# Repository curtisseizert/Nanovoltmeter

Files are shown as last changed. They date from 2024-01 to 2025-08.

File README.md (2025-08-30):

# Nanovoltmeter
A low noise nanovoltmeter design files and code

The design includes five boards:
1. The nanovoltmeter main board
2. A SMPS daughter board to downconvert the battery voltage to the various power rails used in the design
3. A battery board with BMS for 4S 21700 cells
4. A rear panel board with battery charger
5. A front panel

This repository will also include the source code for the STM32U575 microcontroller that interfaces with the various peripherals.

ADR1399-boardfront
ADR1399-boardrear

Note: The current revision of the board does not work without modifications, but the schematic has been annotated to include these. This project should still be considered in a development state, but the entirety of the design is provided here for anyone seeking to draw upon this work in low-noise, high-resolution voltage sensing projects.

Curent Status
-------------
A revision C to the board is in a stage of occasional development as I finish another project. The new revision will seek to improve the robustness of the design, addressing issues such as the apparent sensitivity to common-mode noise, inadequate power protection leading to cascade failures with certain faults, and minor drift related to battery discharge. I am looking into an improved method of retrieving SPI data from ADC conversions that should allow operation at the maximum sample rate of the AD4030-24 (2 MSPS), to reduce noise and reduce the possibility of aliasing. The revision also includes a minor redesign of the key frontend amplifier to improve gain and stability. The ADR1399 reference option will be removed from this revision.

Version 2.0 of the FW improves handling of results and user inputs, as well as reduces the load on the CPU by making better use of DMA. Unit testing is ongoing and some features are not yet implemented, but they will be coming soon. The command structure uses a SCPI-like syntax but is not fully SCPI-compliant. The improved FW should facilitate more performance testing.

I have built two of these boards, one with an LTC6655 reference, the other with an ADR1399. I have tested the noise and offset performance of the latter both with internal shorts and an external 1 mV reference. Getting both boards to work has required some changes, and I have made the appropriate edits to a revision C schematic though I have not laid this out. The noise and temperature sensitivity of the LTC6655 board is superior for internal shorts. 

Design Background
-----------------

A proof of concept model of the input stage was previously prepared, which showed a flat NSD of approximately 1.2 nV/sqrt(Hz). At 1 sample per second, the peak to peak noise was about 15 nV. The temperature coefficient of the meter was approximately 1 nV/K, but sensitivity to temperature fluctuations was evident and the change in power dissipation as the battery discharged led to a drift of ca. 1 nV/h. This prototype also had a bias current of ~3 nA due to charge injection from the input modulator switch. This revision seeks to change those issues as follows:

1. The main power rails of the board are generated using low noise buck converters (LT8608S) and a Cuk converter on a shielded daughterboard so that the dropout of the on-board LDOs remains consistent through battery discharge
2. Improved layout reduced sensitivity to temperature changes. The input stage is contained in a shielding enclosure and is surrounded by isolation slots. Additionally, the largest power dissipators have been placed outside this shield on opposite sides.
3. The input switching is now handled by a low-capacitance quad MOSFET array (PE4140) using gate drive voltages independently generated with a quad DAC. In a model experiment, it has proven feasible to adjust the DAC switching levels and deadtimes to reduce bias current to <5 pA, though I need to do more work to optimize this aspect.
4. A fast, precision ADC (AD4030-24) now measures the offset error between switching cycles so a 16-bit DAC can control the offset voltage of the input differential amplifier by modulating the channel currents of the input JFETs. In the schematic, the trim range of the DAC is approximately +/-625uV (LSB = 20nV). The low gain of the trimming differential amplifier means the transconductance drops by <1% at the input extremes. This should allow measurement of the trim gain during instrument warmup for single-cycle settling of the control loop.
5. Digital implementation of the control loop also allows one to turn off autozeroing or run the input switching at very low frequencies to minimize charge injection.

Some additional features are:
1. Footprints for two types of voltage references: an ADR1399 for lowest noise/highest stability and an LTC6655 for lower power consumption
2. An optically isolated external trigger input for e.g., synchronizing clocking to powerline cycles.
3. Input protection that engages current limiting to 10 mA (typical, max: 15 mA) at a differential voltage of 2 V for protection against accidentally connecting up to 100V across the terminals. A GDT is included to provide transient protection against higher voltages.
4. Two input ranges: +/-2 mV and +/-20 mV.
5. Reduced power consumption (with LTC6655)

Principle of Operation
----------------------

SimplifiedSchematic

An input modulator (SW1) switch connects input and feedback signals alternately to the terminals of a high-gain, low-noise discrete JFET differential amplifier. The outputs of the differential amplifier are connected to the terminals of an operational amplifier (U10) via a synchronous demodulator (SW2). The output of the frontend is taken from this op amp. The ADC reads the output voltage from each phase of the modulator. If the difference between the two readings is larger than a deadband value, the controller increments or decrements the Vos DAC (U44) as needed to adjust the channel currents in the input differential amplifier to null the offset of the differential amplifier. The channel currents are controlled by a low-gain transconductance stage formed from U20. To null the offset and 1/f noise of the ADC and associated signal conditioning circuitry, a switch at the inputs to the ADC driver reverses the inputs to this block such that the modulator/demodulator operates at an integer multiple of the input switches for the ADC.

This topology has the effect of modulating the offset voltage (and 1/f noise) of the input stage up to the switching frequency but not modulating the input signal itself. This modulated error signal is minimized by the offset-nulling feedback loop, which dramatically reduces the power at the chopping frequency, and filtered using a cascaded integrator-comb (sinc) filter of user-selectable order (from 1 to 3). Because the input capacitance of the input stage JFETs is fairly large (ca. 75pF), nulling the offset of the differential amplifier also reduces current pulsation at the chopping frequency.

As such, the only theoretical source of offset, drift, or 1/f noise is the op amp connected to the demodulated differential amp outputs, and all these error sources are attentuated by the gain of the differential amplifier, which is about 3500. The input JFETs are paired with PNP BJTs Q16 and Q21 in a Szlikai-like topology to increase the transconductance of the input amplifier to enable it to operate at high gain. The value of drain resistors R91 and R100 is a compromise between noise, gain, and stability; at 133R, each of the eight JFETs operates with a drain current of ca. 1 mA, and the BJTs operate with a collector current of about 1 mA each. Larger resistor values slightly increase moise, increase gain, and decrease phase margin of the overall composite amplifier due to the increase in loop gain.  The op amp used in the design (an ADA4625-1) is a precision, low noise part with low offset and drift, and these error sources are negligible when attenuated by a factor of 3500. With typical spec sheet values, this op amp should contribute about 4 nV offset, 0.06 nV/K temperature coefficient, and give a 1/f noise corner of ca. 0.1 mHz. In practice, the effect of parasitics, especially thermal EMF proves to be a much larger error source, with an uncorrected offset voltage at the front panel of about 250 nV and a 1/f corner of slightly less than 1 mHz (depending on the stability of the ambient temperature). The NSD when measuring the (internally) shorted inputs is <1.2 nV/rt Hz, and with 10s sample periods I have observed p-p noise of just 1.36 nV over 10000 seconds.

ShortNoise_LTC6655_sinc2

Observations
------------

Modulator frequencies in the 600 - 2000 Hz seem to be ideal, and 1800 Hz is set as the default. The inclusion of the deadband in the offset correction loop is necessary to prevent artifacts that appear in the spectrum of the analog output. The key issue seems to be sensitivity to some noise source at low frequency (probably the SMPS, perhaps also 60 Hz pickup). Modulator frequencies up to 14.4 kHz are possible, but these lead to increases in noise as the settling time of the frontend and ADC signal conditioning circuits takes up an increasing percentage of the potential conversion time.

NVM B no deadband, 1 LSB inc, offsets
NSD without deadband, showing aliasing of V_os correction loop

The biggest limitation in the utility of the instrument is the considerable increase in noise and change in offset that occurs when something is connected to the front panel. This effect occurs regardless of whether the input relay is measuring an internal short. It seems most likely that the case, which is tied to protective earth via the USB cable shield is shifting in potential relative to circuit ground, and this is capacitively coupling to something sensitive. However, connecting the USB cable through an isolator, which disconnects the shield from PE, actually makes the noise situation worse rather than better. 

Implementation of a Sinc2 filter improved some apparent aliasing artifacts that were present in the spectrum at very low (<10 mHz) frequencies. Use of a Sinc3 filter did not lead to any noticeable improvents. The flatness of the noise spectrum (with an internal short) to below 1 mHz was very repeatable provided that environmental conditions were suitably stable.

ShortNoise_LTC6655_sinc1
ShortNoise_LTC6655_sinc2

While the nanovoltmenter has an offset temperature coefficient of <1 nV/K, it does show some sensitivity to changes in the rate of temperature change (i.e., the offset voltage correlates to the second derivative of temperature with respect to time). This makes sense because those changes lead to changes in temperature gradients across the board, which influences parasitic thermocouple behavior at the input. The power supply is also somewhat more efficient at lower input voltages, which leads to reduced heat dissipation as the batteries discharge, influencing the offset. In very long captures, such as the LTC6655 reference example shown below, this leads to a drift of <0.1 nV/h. It is notable that the overall drift in this 100h capture was only about 8 nV despite about 2.5 K fluctuation in input temperature over that time.

LongCapture_LTC6655_0p01SPS_sinc2
LongCapture_ADR1399_0p01SPS

The linearity of the amplifier is expected to be quite good as the offset correction loop keeps the input terminals of the frontend amplifier at the same voltage regardless of input. The main source of nonlinearity should be the gain setting resistors, as temperature changes due to increased power dissipation may lead to changes the resistor ratio and the gain of the frontend. To test the linearity of the amplifier, I used a highly accurate source based on an LTZ1000A and DAC11001B with a tested linearity error of <2 ppm and a 200K/20R divider to reduce the output voltage range to 0 to 1 mV. I averaged several 11 point sweeps over this range to obtain a maximum linearity error of 1.5 ppm. The averaging was necessary due the increased noise seen with something plugged in to the front panel. The increased sensitivity of the lower gain +/-20 mV range to external noise sources (probably due to reduced stability of the amplifier at lower gain) meant that determining linearity error for this range was not practical. In all measurements of external sources, I found it was optimal to wrap the test lead around a nanocrystalline toroid, which did reduce noise considerably.

LinearitySweep

Performance Reductions with External Measurements
-------------------------------------------------

Taken together, my observations about the difficulty of performing measurements with external sources are difficult to untangle and may point to multiple simultaneous issues. I have collected them here to try to provide some insight into this behavior and possible solutions:
1. The 40 dB gain range is more sensitive than the 60 dB gain range. The lower gain range has lower phase margin and still takes 60 dB gain at higher frequencies, as this was necessary to ensure stability of the amplifier at lower gain. This points to stability related problems, such as degradation of phase margin (leading to ringing, etc. after switching events) when the amplifier sees an inductive source impedance. Inductive sources present a considerable challenge with such amplifiers because of the large gate-source capacitance of the paralleled JFETs. This can give resonant gain with inductive inputs.
2. The improvement in performance when using a common mode choke on the input suggests an effect from frequencies well above the amplifier's passband. The inductance of the common mode choke was likely aorund 800 uH, which would present negligible impedance at 60 Hz.
3. I recorded spectra from the analog outputs with the instrument powered by a bench power supply to remove SMPS signals. With 60 dB gain on the frontend and the 10 nF input capacitor switched off, the peaks at harmonics of the chopping frequency were about 20 dB higher with an external short than with an internal short. This is presumably an effect of inductance at the input as there are ferrite beads in the input protection circuitry between the internal and external shorts. Some of these artifacts may lead to aliasing.
Internal Short Analog Output, Gain = 1000
NVM B Internal short Gain1000 Linear supply CapOff
External Short Analog Output, Gain = 1000NVM B External short Gain1000 Linear supply CapOff
4. Plugging a source into the input leads to a shift in offset with an internal short (ca. 200 nV). The source of this effect is not clear. The source mentioned in the linearity test section actually has an internal 100:1 attenuator for low voltages, but directly plugging the source into the NVM gave such large increases in noise that it would not be practical to measure ppm level offsets. The input connector is a LEMO-0S-304 type with the shell of the connector electically connected to the instrument chassis, which is itself connected to protective earth via the USB cable. In general, cables with the shield connected at both ends gave significantly poorer performance than those with the shield left unconnected at one end, suggesting that connection of the two chassis grounds was problematic despite their isolation from circuit ground. The use of nylon screws to connect the USB connector to the rear panel of the source (and hence remove the connection to protective earth) was necessary for reliable results in that case. Most of the sensitive circuitry of the input is very well shielded against electrostatic pickup by the use of board-level RF shields, but the input protection circuitry and switching relays, as well as the chopper demodulator and op amp, are outside of these shields. A ground loop is not necesasary to cause this effect, as it is observed even when an unconnected cable is plugged into the front panel. Some additional tests are necessary to determine the minimum configuration needed to cause this shift (e.g., does the behavior occur with just connection of the shell, or do the actual input leads (which provide a connection to the board) need to be connected as well? If it seems that additional shielding is needed to reduce this effect, it may be difficult to maintain the same form factor.

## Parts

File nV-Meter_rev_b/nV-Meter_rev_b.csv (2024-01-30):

Source: | C:\Users\Curtis\Documents\KiCAD\1fNoiseAmp\1fNoiseAmpRev12\1fNoiseAmpRev12.kicad_sch
Date: | 7/12/2023 12:35:11 AM
Tool: | Eeschema (6.0.11)
Generator: | C:\Program Files\KiCad\6.0\bin\scripting\plugins/bom_csv_grouped_by_value_with_fp.py
Component Count: | 376
Ref | Qnty | Value | Cmp name | Footprint | Description | Vendor
C1, C2, C3, C4, C5, C6, C7, C8, C11, C12, C13, C14, C16, C17, C18, C19, C20, C21, C66, C67, C84, | 21 | 100nF | C_Small | Capacitor_SMD:C_1206_3216Metric_Red | Unpolarized capacitor, small symbol
C9, C10, C15, C91, C92, | 5 | 47uF/16V | CP1_Small | Capacitor_Tantalum_SMD:CP_EIA-3528-12_Kemet-T | Polarized capacitor, small US symbol
C22, C23, C25, C26, C94, | 5 | 100nF X7R | C_Small | Capacitor_SMD:C_0603_1608Metric_red_outline | Unpolarized capacitor, small symbol
C24, C27, C28, C29, C30, C31, C32, C33, C34, C35, C36, C37, C38, C39, C40, C41, C42, C43, C44, C45, C46, C48, C49, C51, C52, C57, C64, C85, | 28 | 10nF | C_Small | Capacitor_SMD:C_0603_1608Metric_red_outline | Unpolarized capacitor, small symbol
C47, C63, | 2 | 10x470nF | C_Small | Capacitor_SMD:C_1206x10_3216Metric_Red | Unpolarized capacitor, small symbol
C50, | 1 | 33pF | C_Small | Capacitor_SMD:C_0603_1608Metric_red_outline | Unpolarized capacitor, small symbol | 81-GRM185C1H330GA01J
C53, C54, | 2 | 10pF C0G | C_Small | Capacitor_SMD:C_0603_1608Metric_red_outline | Unpolarized capacitor, small symbol
C55, C61, | 2 | 1nF | C_Small | Capacitor_SMD:C_0603_1608Metric_red_outline | Unpolarized capacitor, small symbol
C56, C62, | 2 | 47nF | C_Small | Capacitor_SMD:C_0805_2012Metric_Red_outline | Unpolarized capacitor, small symbol
C58, C65, | 2 | 470nF | C_Small | Capacitor_SMD:C_1206_3216Metric_Red | Unpolarized capacitor, small symbol
C59, C60, C78, | 3 | 10nF C0G | C_Small | Capacitor_SMD:C_0603_1608Metric_red_outline | Unpolarized capacitor, small symbol
C68, C69, | 2 | 10uF/25V | CP1_Small | Capacitor_Tantalum_SMD:CP_EIA-3528-12_Kemet-T | Polarized capacitor, small US symbol
C70, C71, | 2 | 33uF/25V | CP1_Small | Capacitor_Tantalum_SMD:CP_EIA-7343-31_Kemet-D | Polarized capacitor, small US symbol
C72, C73, | 2 | 10uF/35V | C_Small | Capacitor_SMD:C_1210_3225Metric | Unpolarized capacitor, small symbol
C74, C80, | 2 | 2.2uF X7R | C_Small | Capacitor_SMD:C_0805_2012Metric_Red_outline | Unpolarized capacitor, small symbol
C75, C76, | 2 | 22uF/50V | CP1_Small | Capacitor_Tantalum_SMD:CP_EIA-7343-31_Kemet-D | Polarized capacitor, small US symbol
C77, C79, | 2 | 10uF/25V | CP1_Small_Kelvin | Capacitor_Tantalum_SMD:CP_EIA-3528-12_Kemet-T_Kelvin | Polarized capacitor, small US symbol
C81, | 1 | 63x470nF/25V | C_Small | Capacitor_SMD:C_1206_Parallel | Unpolarized capacitor, small symbol
C82, | 1 | DNP | C_Small | Resistor_SMD:R_0603_1608Metric_red | Unpolarized capacitor, small symbol
C83, | 1 | 47nF/25V | C_Small | Capacitor_SMD:C_0805_2012Metric_Red_outline | Unpolarized capacitor, small symbol
C86, | 1 | 3.3pF C0G | C_Small | Capacitor_SMD:C_0603_1608Metric_red_outline | Unpolarized capacitor, small symbol | 81-GCM1885C2A3R3BA6D
C87, C88, C89, C90, | 4 | 100nF/50V | C_Small | Capacitor_SMD:C_1206_3216Metric_Red | Unpolarized capacitor, small symbol
C93, | 1 | 68pF C0G | C_Small | Capacitor_SMD:C_0603_1608Metric_red_outline | Unpolarized capacitor, small symbol | 81-GCM1885C2A680FA6D
D1, D2, D3, | 3 | ESDA6V1-5SC6 | ESDA6V1-5SC6 | Package_TO_SOT_SMD:SOT-23-6 | Quintuple bidirectional transil, Suppressor for ESD protection, 6V1 Breakdown, SOT-23-6
D4, D5, D6, D7, D8, D9, D10, D11, D19, D20, | 10 | DZ2S100X0L | DZ2S100X0L | Diode_SMD:D_SOD-523 | 150mW Silicon Planar Zener Diode, 10V, SOD-523 | 755-EDZVFHT2R10B
D12, D13, D14, D15, D17, D18, D22, D25, | 8 | BAV199 | BAV99 | Package_TO_SOT_SMD:SOT-23 | BAV99 High-speed switching diodes, SOT-23
D16, | 1 | LED | LED | LED_SMD:LED_Dialight_591 | Light emitting diode
D21, | 1 | BAV199DW | BAV199DW | Package_TO_SOT_SMD:SOT-363_SC-70-6 | Quad Surface Mount Low Leakage Diode, SOT-363
D23, D24, | 2 | MBR0540 | MBR0540 | Diode_SMD:D_SOD-123 | 40V 0.5A Schottky Power Rectifier Diode, SOD-123
H1, H2, H3, H4, | 4 | MountingHole_Pad | MountingHole_Pad | MountingHole:MountingHole_2.2mm_M2_Pad_Via | Mounting Hole with connection
J1, | 1 | Conn_Coaxial | Conn_Coaxial | Connector_Coaxial:SMA_Molex_73251-2120_EdgeMount_Horizontal | coaxial connector (BNC, SMA, SMB, SMC, Cinch/RCA, LEMO, ...)
J2, | 1 | Conn_01x02 | Conn_01x02 | Connector_PinHeader_2.54mm:PinHeader_1x02_P2.54mm_Vertical | Generic connector, single row, 01x02, script generated (kicad-library-utils/schlib/autogen/connector/)
J3, | 1 | IDC_HDR | Conn_02x10_Odd_Even | Connector_PinHeader_1.27mm:PinHeader_2x10_P1.27mm_Vertical | Generic connector, double row, 02x10, odd/even pin numbering scheme (row 1 odd numbers, row 2 even numbers), script generated (kicad-library-utils/schlib/autogen/connector/)
J4, | 1 | PIN_JMP | Conn_02x03_Odd_Even | Connector_PinHeader_2.54mm:PinHeader_2x03_P2.54mm_Vertical | Generic connector, double row, 02x03, odd/even pin numbering scheme (row 1 odd numbers, row 2 even numbers), script generated (kicad-library-utils/schlib/autogen/connector/)
J5, J23, | 2 | Conn_Coaxial | Conn_Coaxial | Connector_Coaxial:SMA_Molex_73251-135_SMT_Vertical | coaxial connector (BNC, SMA, SMB, SMC, Cinch/RCA, LEMO, ...)
J6, J7, J8, J9, J10, J11, J12, J13, J14, J15, J16, J17, | 12 | ShieldClip | Conn_01x01 | RF_Shielding:RF_Shield_Clip_Harwin_Mini | Generic connector, single row, 01x01, script generated (kicad-library-utils/schlib/autogen/connector/)
J18, J19, | 2 | RF_Shield_Two_Pieces | RF_Shield_Two_Pieces | RF_Shielding:Laird_Technologies_BMI-S-230-F_50.8x38.1mm | Two-piece EMI RF shielding cabinet | 739-BMI-S-230-F
J20, J21, | 2 | SMA_OUT | Conn_Coaxial | Connector_Coaxial:SMA_Molex_73251-2120_EdgeMount_Horizontal | coaxial connector (BNC, SMA, SMB, SMC, Cinch/RCA, LEMO, ...)
J22, | 1 | Micro-Fit 3.0 43650-0310 | Conn_01x03_MountingPin | Connector_Molex:Molex_Micro-Fit_3.0_43650-0310_1x03-1MP_P3.00mm_Horizontal_PnP | Generic connectable mounting pin connector, single row, 01x03, script generated (kicad-library-utils/schlib/autogen/connector/) | 538-43650-0310
K1, K2, K3, K4, | 4 | G6KU-2 | G6KU-2 | Relay_SMD:Relay_DPDT_Omron_G6K-2G-Y | Miniature 2-pole relay, Single-winding Latching | 653-G6KU-2G-Y-DC5
Q1, Q3, Q5, Q7, Q22, | 5 | BSS84 | BSS84 | Package_TO_SOT_SMD:SOT-23 | -0.13A Id, -50V Vds, P-Channel MOSFET, SOT-23
Q2, Q4, Q6, Q8, | 4 | BSS123 | BSS123 | Package_TO_SOT_SMD:SOT-23 | 0.17A Id, 100V Vds, N-Channel MOSFET, SOT-23
Q9, Q10, Q11, Q14, Q15, | 5 | MMBF4117 | MMBF4117 | Package_TO_SOT_SMD:SOT-23 | Low leakage N-Channel JFET, SOT-23
Q12, | 1 | SiS443DN | SiS443DN | Package_SO:Vishay_PowerPAK_1212-8_Single | -35A Id, -40V Vds, P-Channel MOSFET, PowerPAK 1212-8 Single
Q13, | 1 | SiS862ADN | SiS862ADN | Package_SO:Vishay_PowerPAK_1212-8_Single | 52A Id, 60V Vds, 7.2mOhm Rds(ON), N-Channel MOSFET, PowerPAK 1212-8 Single
Q16, Q17, Q20, Q24, Q27, Q29, Q31, Q33, Q35, Q37, Q39, Q41, Q43, Q45, Q47, Q49, Q51, Q53, | 18 | MMBT3904 | MMBT3904 | Package_TO_SOT_SMD:SOT-23 | 0.2A Ic, 40V Vce, Small Signal NPN Transistor, SOT-23
Q18, Q23, Q26, Q28, Q30, Q32, Q34, Q36, Q38, Q40, Q42, Q44, Q46, Q48, Q50, Q52, | 16 | JFE2140 | JFE2140 | Package_SO:SOIC-8_3.9x4.9mm_P1.27mm | Ultra-low Noise, Matched, Dual, Low-Gate Current, Discrete Audio N-Channel JFET
Q19, | 1 | HN4C51J | HN4C51J | Package_TO_SOT_SMD:SOT-23-5_red | 120V 100mA Common Base Audio Frequency GP NPN Pair
Q21, Q25, | 2 | HN4A51J | HN4A51J | Package_TO_SOT_SMD:SOT-23-5_red | 120V 100mA Common Base Audio Frequency GP PNP Pair
R1, | 1 | 6k02 0.1% | R_US | Resistor_SMD:R_1206_3216Metric_red | Resistor, US symbol | 667-ERA-8AEB6041V
R2, | 1 | 240R 0.1% | R_US | Resistor_SMD:R_1206_3216Metric_red | Resistor, US symbol | 667-ERA-8AEB241V
R3, R67, R68, | 3 | 0R5 | R_US | Resistor_SMD:R_1206_3216Metric_red | Resistor, US symbol
R4, R5, R6, R7, R8, R9, R12, R13, R14, R15, R58, | 11 | 10k | R_US | Resistor_SMD:R_0603_1608Metric_red | Resistor, US symbol
R10, R11, R16, R17, R18, R19, R20, R21, R22, R23, R63, R64, R90, R91, | 14 | 1M | R_US | Resistor_SMD:R_0603_1608Metric_red | Resistor, US symbol
R24, R25, R54, R55, R56, R59, R60, R100, R111, | 9 | 49R9 | R_US | Resistor_SMD:R_0603_1608Metric_red | Resistor, US symbol
R26, | 1 | 10M | R_US | Resistor_SMD:R_1206_3216Metric_red | Resistor, US symbol
R27, R28, R103, | 3 | 1k 0.1% | R_US | Resistor_SMD:R_0805_2012Metric_red | Resistor, US symbol
R29, | 1 | 49R9 0.1% | R_US | Resistor_SMD:R_0805_2012Metric_red | Resistor, US symbol
R30, R31, R49, R51, R86, | 5 | 1k | R_US | Resistor_SMD:R_0603_1608Metric_red | Resistor, US symbol
R32, | 1 | 47R5 | R_US | Resistor_SMD:R_0805_2012Metric_red | Resistor, US symbol | 667-ERA-6AEB47R5V
R33, | 1 | 1k24 0.1% | R_US | Resistor_SMD:R_0805_2012Metric_red | Resistor, US symbol | 71-TNPW08051K24BEEA
R34, | 1 | 240R 0.1% | R_US | Resistor_SMD:R_0805_2012Metric_red | Resistor, US symbol | 754-RG2012N-241-WT1
R35, | 1 | 220R | R_US | Resistor_SMD:R_0805_2012Metric_red | Resistor, US symbol | 667-ERA-6VEB2200V
R36, | 1 | 2k67 | R_US | Resistor_SMD:R_0603_1608Metric_red | Resistor, US symbol | 754-RR0816P-2671D42H
R37, | 1 | 56k2 | R_US | Resistor_SMD:R_0603_1608Metric_red | Resistor, US symbol | 754-RR0816P-5622D73C
R38, | 1 | 2k4 0.1% | R_US | Resistor_SMD:R_0805_2012Metric_red | Resistor, US symbol | 667-ERA-6ARW242V
R39, | 1 | 9k53 | R_US | Resistor_SMD:R_0603_1608Metric_red | Resistor, US symbol
R40, R84, | 2 | 200k | R_US | Resistor_SMD:R_0603_1608Metric_red | Resistor, US symbol | 754-RR0816P-204D
R41, | 1 | 2M87 | R_US | Resistor_SMD:R_0603_1608Metric_red | Resistor, US symbol
R42, R43, | 2 | 2M49 | R_US | Resistor_SMD:R_0603_1608Metric_red | Resistor, US symbol | 603-RC0603FR-072M49L
R44, | 1 | 1M8 | R_US | Resistor_SMD:R_0603_1608Metric_red | Resistor, US symbol | 603-AC0603FR-071M8L
R45, R97, | 2 | 887R | R_US | Resistor_SMD:R_0603_1608Metric_red | Resistor, US symbol | 754-RR0816P-8870D92A
R46, | 1 | 18k7 | R_US | Resistor_SMD:R_0603_1608Metric_red | Resistor, US symbol | 754-RR0816P-1872D27C
R47, R76, R77, R82, | 4 | 28k7 | R_US | Resistor_SMD:R_0603_1608Metric_red | Resistor, US symbol
R48, | 1 | 604k | R_US | Resistor_SMD:R_0603_1608Metric_red | Resistor, US symbol | 603-RT0603DRE07604KL
R50, R61, R62, | 3 | 100k | R_US | Resistor_SMD:R_0603_1608Metric_red | Resistor, US symbol
R52, | 1 | 499k | R_US | Resistor_SMD:R_1206_3216Metric_red | Resistor, US symbol | 667-ERA-8AEB4993V
R53, | 1 | 4M7 | R_US | Resistor_SMD:R_1206_3216Metric_red | Resistor, US symbol | 594-MCA1206MD4704BP1
R57, | 1 | 10M | R_US | Resistor_SMD:R_0603_1608Metric_red | Resistor, US symbol
R65, R66, | 2 | 2R | R_US | Resistor_SMD:R_0603_1608Metric_red | Resistor, US symbol
R69, | 1 | 43k 0.1% | R_US | Resistor_SMD:R_1206_3216Metric_red | Resistor, US symbol | 667-ERA-8AEB433V
R70, | 1 | 53k6 | R_US | Resistor_SMD:R_1206_3216Metric_red | Resistor, US symbol | 667-ERA-8AEB53R6V
R71, | 1 | 499k | R_US | Resistor_SMD:R_0603_1608Metric_red | Resistor, US symbol
R72, R74, | 2 | 30k1 | R_US | Resistor_SMD:R_0603_1608Metric_red | Resistor, US symbol
R73, | 1 | 360k | R_US | Resistor_SMD:R_0603_1608Metric_red | Resistor, US symbol | 754-RR0816P-364D
R75, | 1 | 100M | R_US | Resistor_SMD:R_1206_3216Metric_red | Resistor, US symbol | 708-HVCB1206FKC100M
R78, | 1 | 7k5 | R_US | Resistor_SMD:R_0603_1608Metric_red | Resistor, US symbol | 754-RR0816P-752D
R79, R81, R85, R89, R92, R94, R95, R96, R98, R99, R102, R105, R106, R107, R108, R109, R110, | 17 | 3k3 | R_US | Resistor_SMD:R_0603_1608Metric_red | Resistor, US symbol | 754-RR0816P-332D
R80, R83, | 2 | 330 0.1% | R_US | Resistor_SMD:R_0805_2012Metric_red | Resistor, US symbol
R87, R88, | 2 | 33k 0.1% | R_US | Resistor_SMD:R_0805_2012Metric_red | Resistor, US symbol
R93, | 1 | 100R | R_US | Resistor_SMD:R_0603_1608Metric_red | Resistor, US symbol
R101, | 1 | 4R7 | R_US | Resistor_SMD:R_0603_1608Metric_red | Resistor, US symbol | 603-RT0603FRE074R7L
R104, | 1 | 4R99 0.1% | R_US | Resistor_SMD:R_0805_2012Metric_red | Resistor, US symbol
RN1, RN2, RN3, | 3 | 33R | R_Pack04 | Resistor_SMD:R_Array_Convex_4x0402 | 4 resistor network, parallel topology
RN4, | 1 | 9k/1k | Voltage_Divider | Package_TO_SOT_SMD:SOT-23 | Voltage divider | 71-MPMT10019001AT1
RN5, RN6, | 2 | 10k/10k | Voltage_Divider | Package_TO_SOT_SMD:SOT-23 | Voltage divider
RN7, RN8, RN9, | 3 | 1M | R_Pack04 | Resistor_SMD:R_Array_Convex_4x0402 | 4 resistor network, parallel topology
TP1, TP2, TP3, TP4, TP5, TP6, TP7, TP8, TP9, TP10, TP11, TP12, TP13, TP14, TP15, TP16, TP17, TP18, TP19, TP20, TP21, TP22, TP23, TP24, TP25, TP26, TP27, TP28, TP29, TP30, TP31, | 31 | TestPoint | TestPoint | TestPoint:TestPoint_Pad_D1.0mm | test point
U1, U2, U4, | 3 | TLV1812D | TLV1812D | Package_SO:SOIC-8_3.9x4.9mm_P1.27mm | Dual Rail-to-Rail Input Comparators with Push-Pull Output, SOIC-8
U3, U7, U12, U15, U16, | 5 | DG636EEQ | DG636EEQ_4 | Package_SO:TSSOP-14_4.4x5mm_P0.65mm | 0.3 pC Charge Injection, 100 pA Leakage
U5, U21, | 2 | OPA140 | OPA140 | Package_SO:MSOP-8_3x3mm_P0.65mm | High-Precision, Low-Noise, RRO, 11 MHz JFET Op Amp
U6, U8, U10, U11, U20, | 5 | ADA4622-2 | OPA2145 | Package_SO:MSOP-8_3x3mm_P0.65mm | Dual Operational Amplifiers, DIP-8/SOIC-8/TSSOP-8/VSSOP-8
U9, U13, | 2 | ADA4807-1 | ADA4807-1 | Package_TO_SOT_SMD:SOT-23-6_red | Single Rail-to-Rail Input/Output Amplifiers, with disable, SC-70-6/SOT-23-6
U14, | 1 | TLC555xD | TLC555xD | Package_SO:SOIC-8_3.9x4.9mm_P1.27mm | Single LinCMOS Timer, 555 compatible, SOIC-8 | 700-ICM7555ISAT
U17, | 1 | LT3042xMSE | LT3042xMSE | Package_SO:MSOP-10EP-3x3_P0.5mm_EP_thermal_vias_opt | 200mA, Adjustable, Ultralow Noise, Ultrahigh PSRR RF Linear Regulator, MSOP-10
U18, | 1 | LP2985-3.3 | LP2985-3.3 | Package_TO_SOT_SMD:SOT-23-5 | 150mA 16V Low-noise Low-dropout Regulator With Shutdown, 3.3V output voltage, SOT-23-5
U19, | 1 | LT3093xMSE | LT3093xMSE | Package_SO:MSOP-12-1EP_3x4mm_P0.65mm_EP1.65x2.85mm_ThermalVias_opt | -200mA, Adjustable, Ultralow Noise, Ultrahigh PSRR RF Negative Linear Regulator, MSOP-12
U22, | 1 | 74AUP1G02 | 74AUP1G02 | Package_TO_SOT_SMD:SOT-353_SC-70-5 | Single NOR Gate, Low-Voltage CMOS | 595-SN74AUP1G02DCKT

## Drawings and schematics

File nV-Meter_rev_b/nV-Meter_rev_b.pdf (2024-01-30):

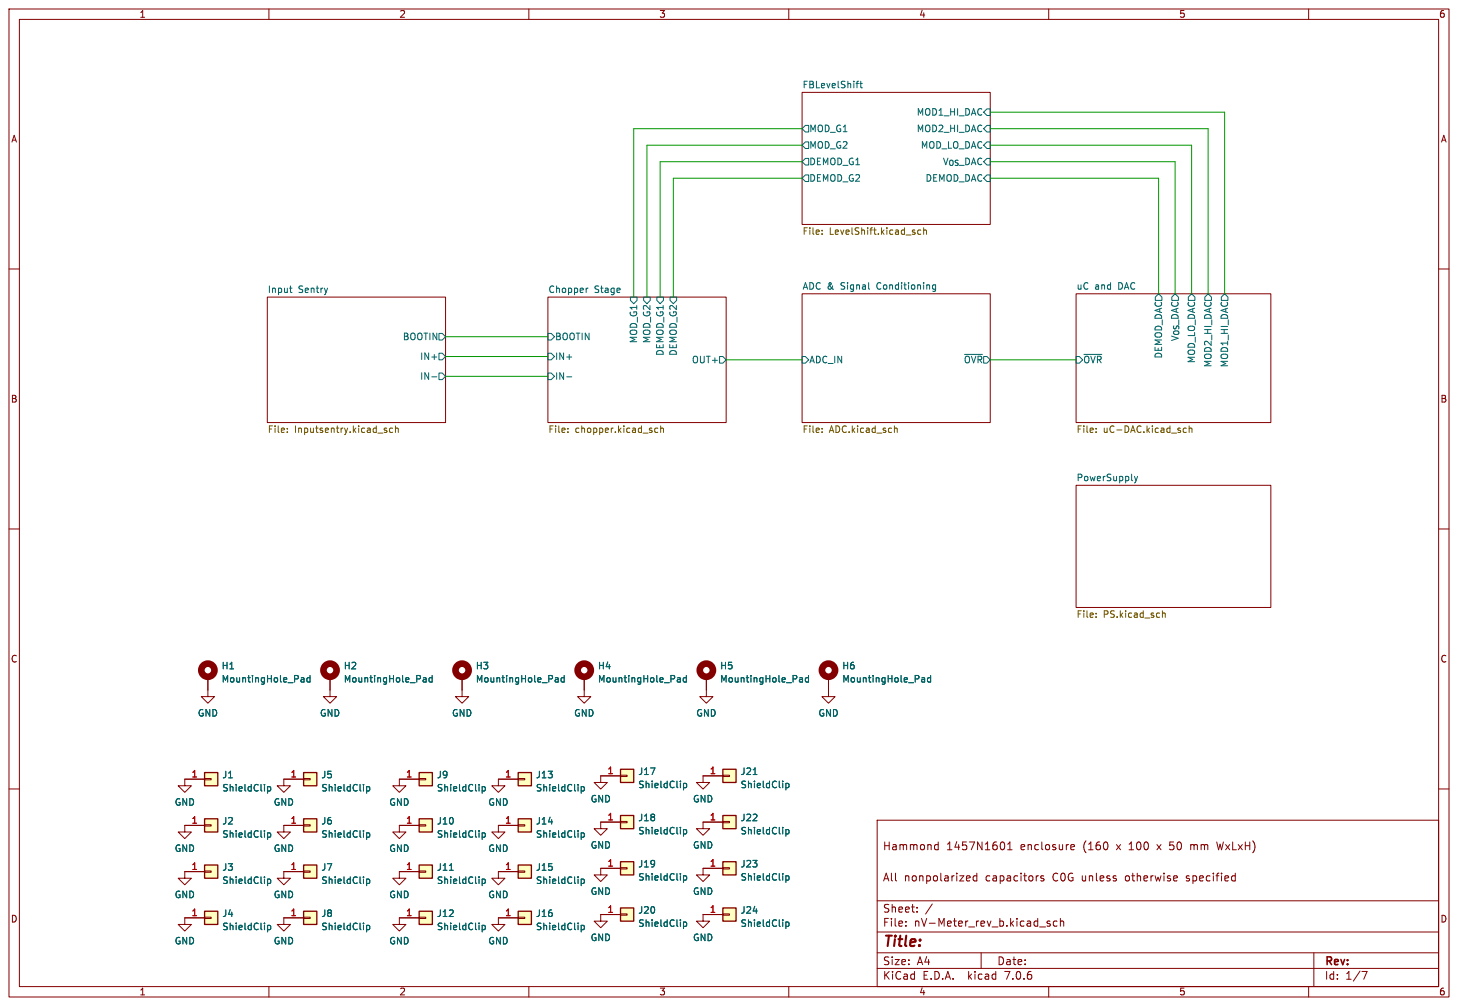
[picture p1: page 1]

Chopper Stage File: chopper.kicad_sch H4 MountingHole_Pad

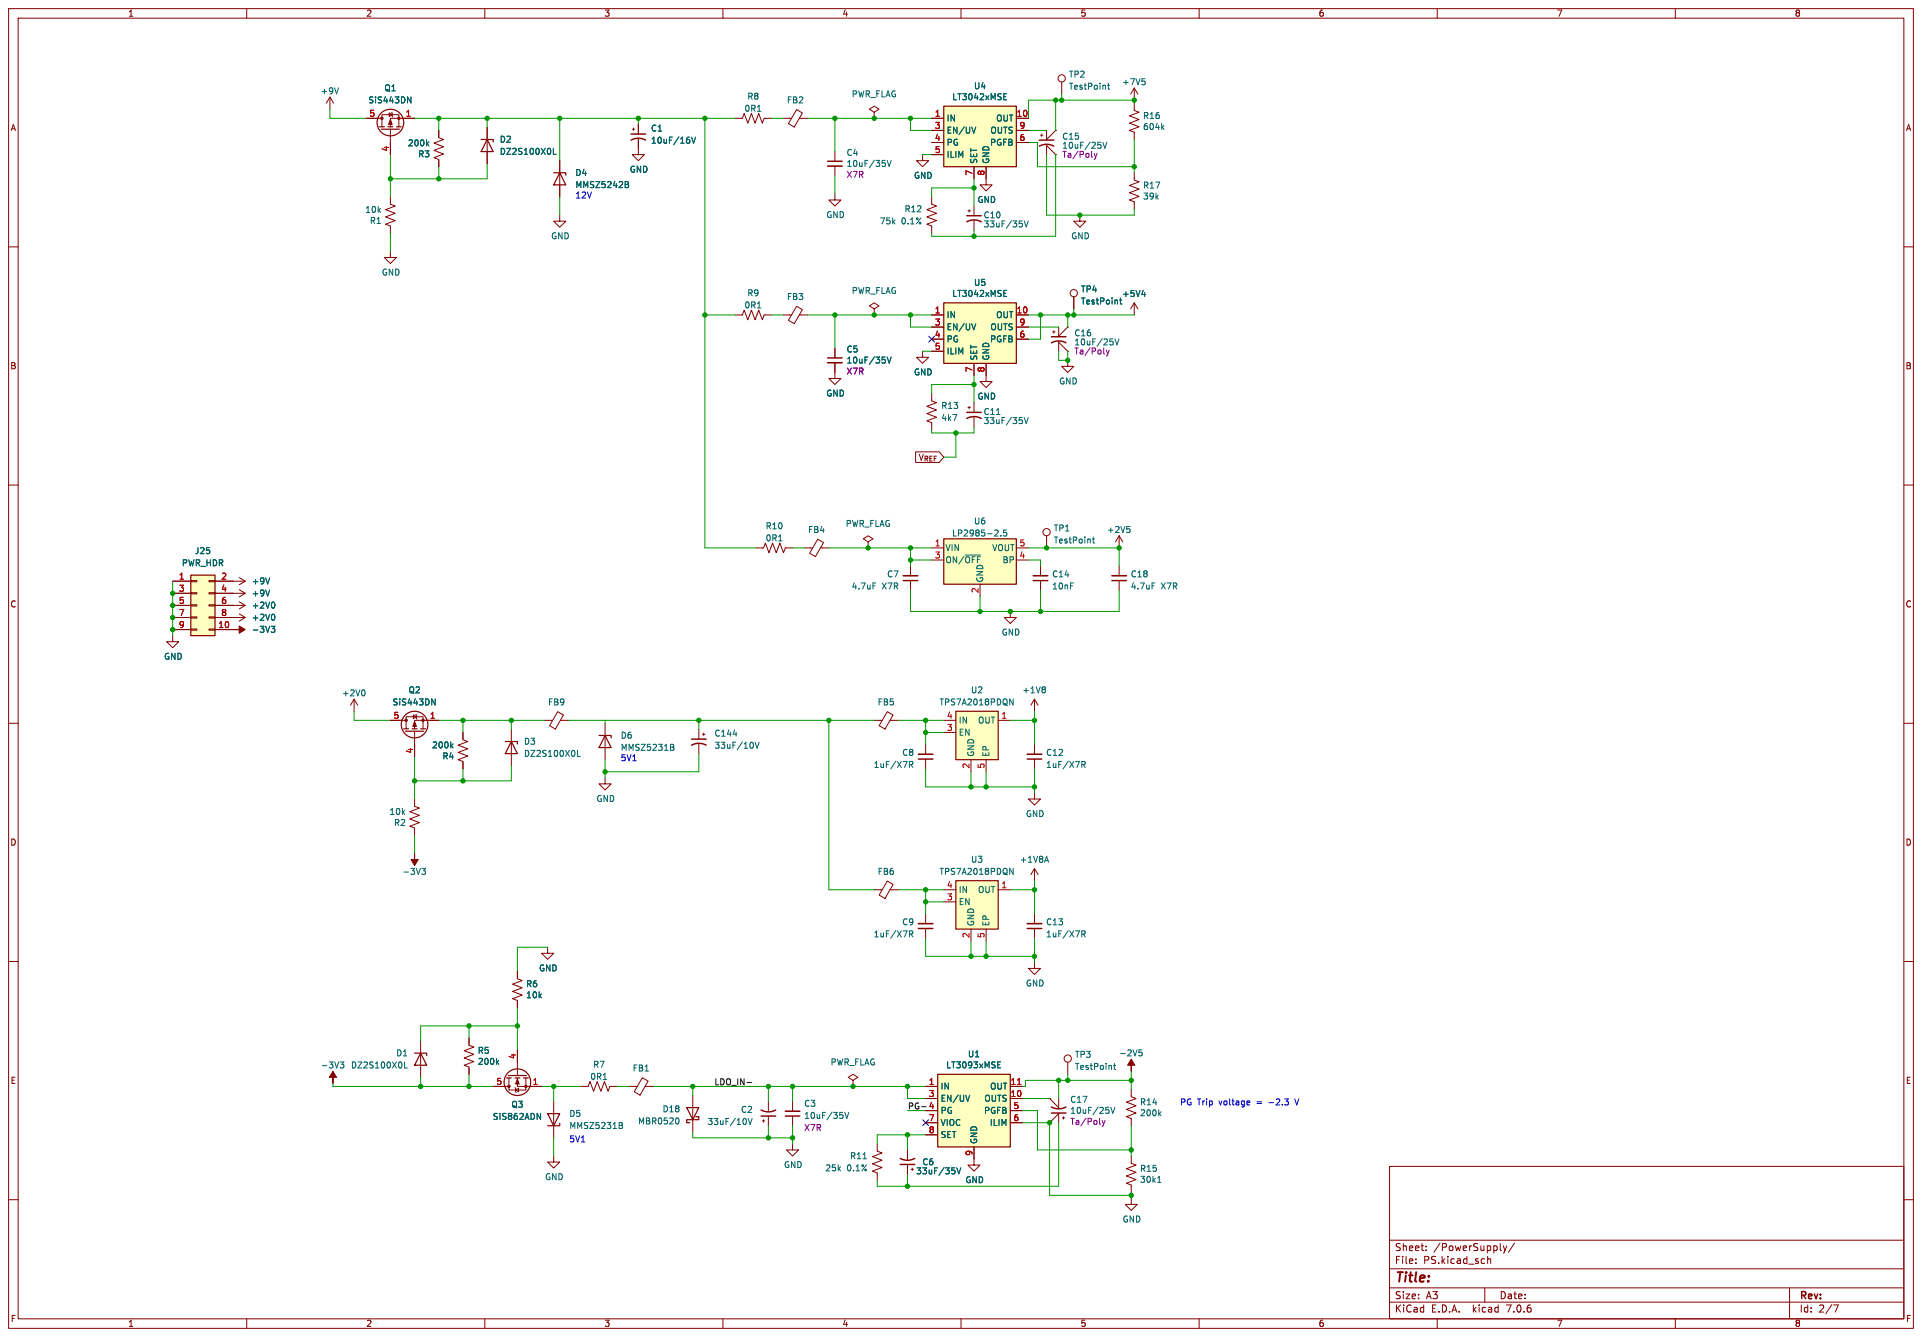
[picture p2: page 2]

2 ON/~{OFF} 3 BP 4 VOUT 5 U6

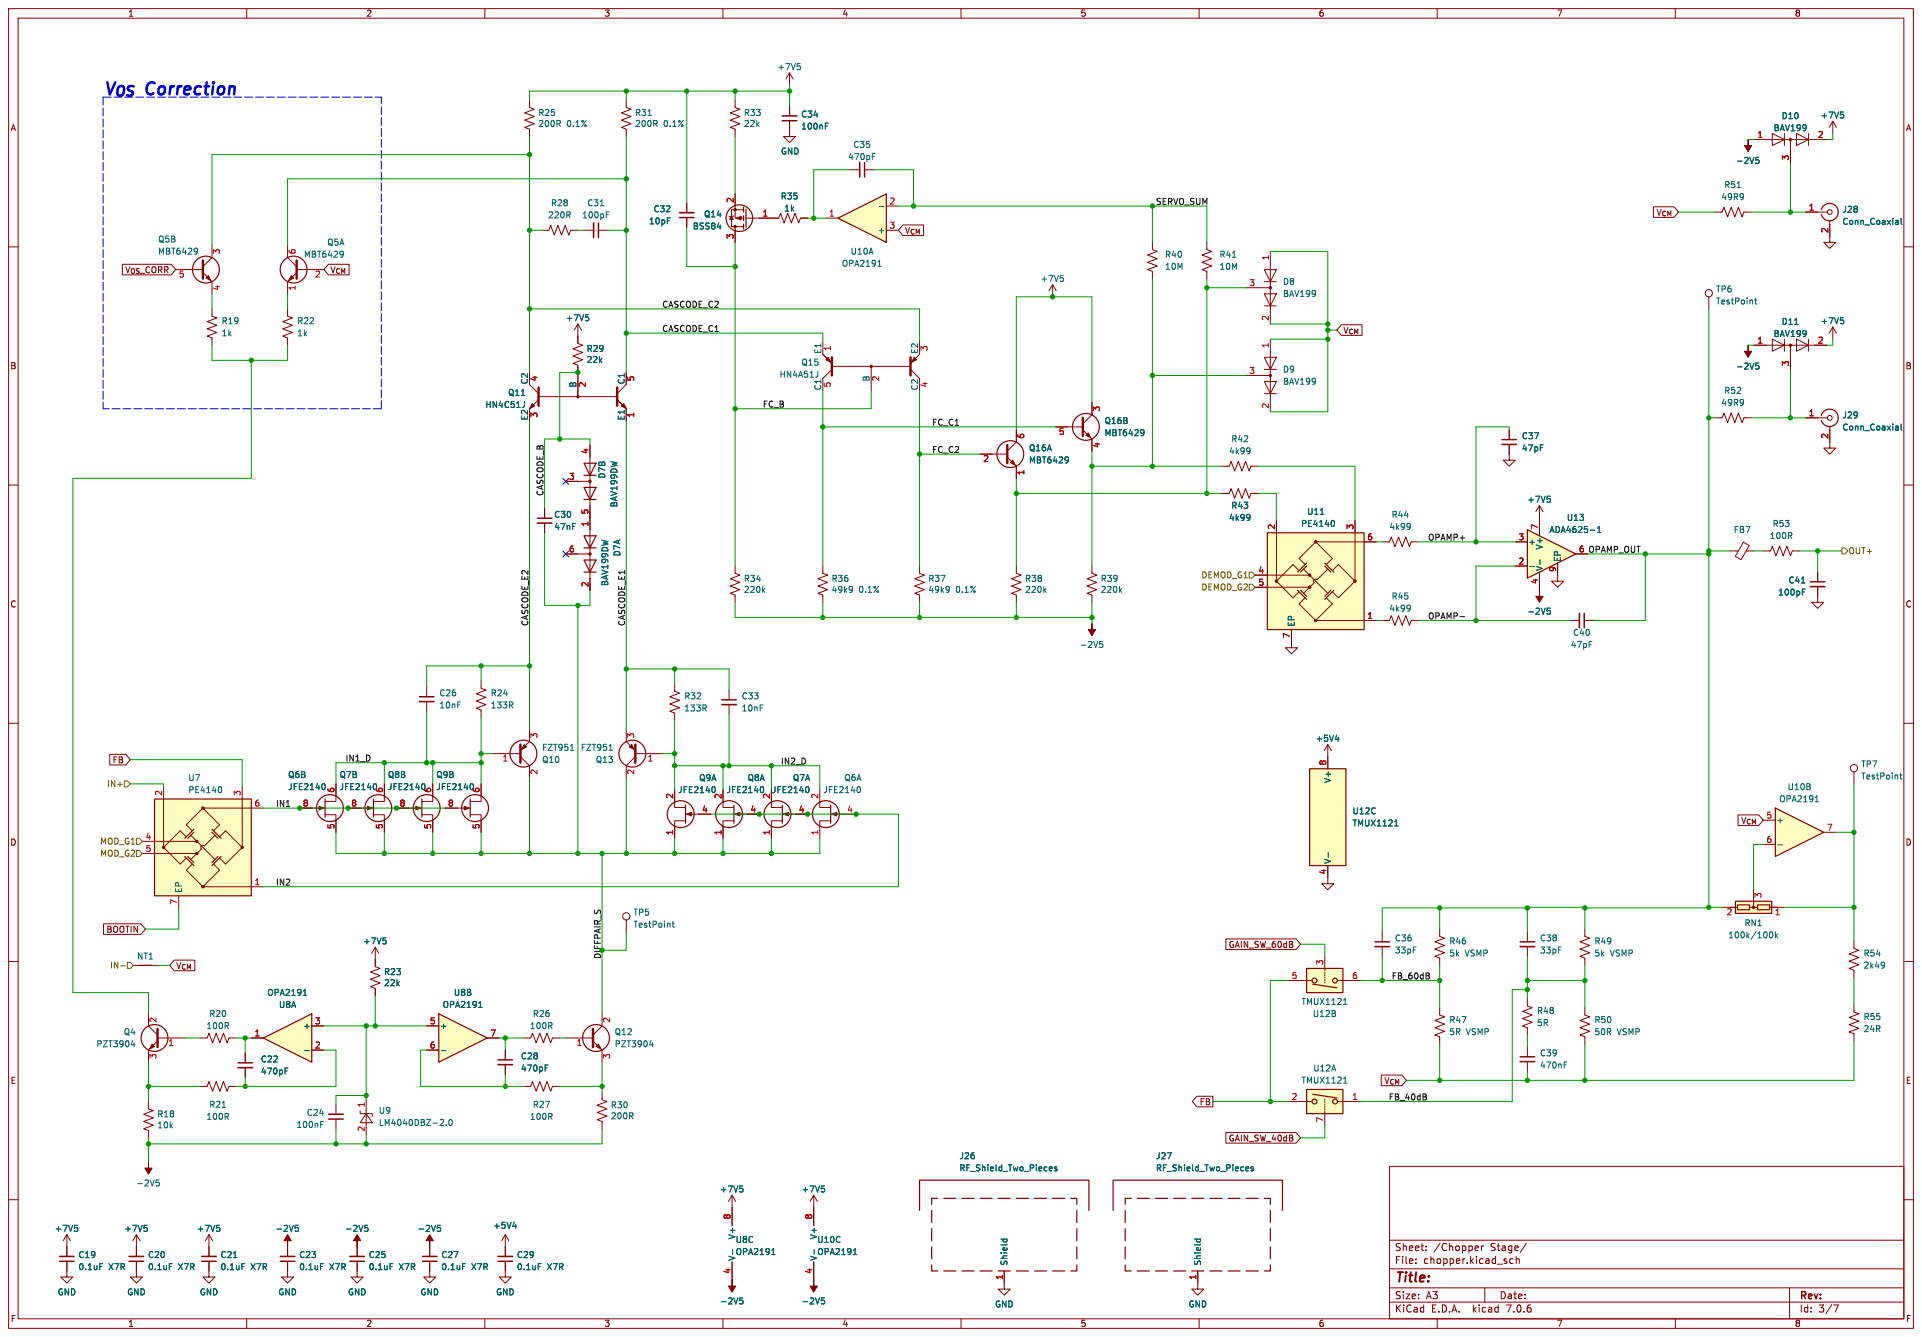
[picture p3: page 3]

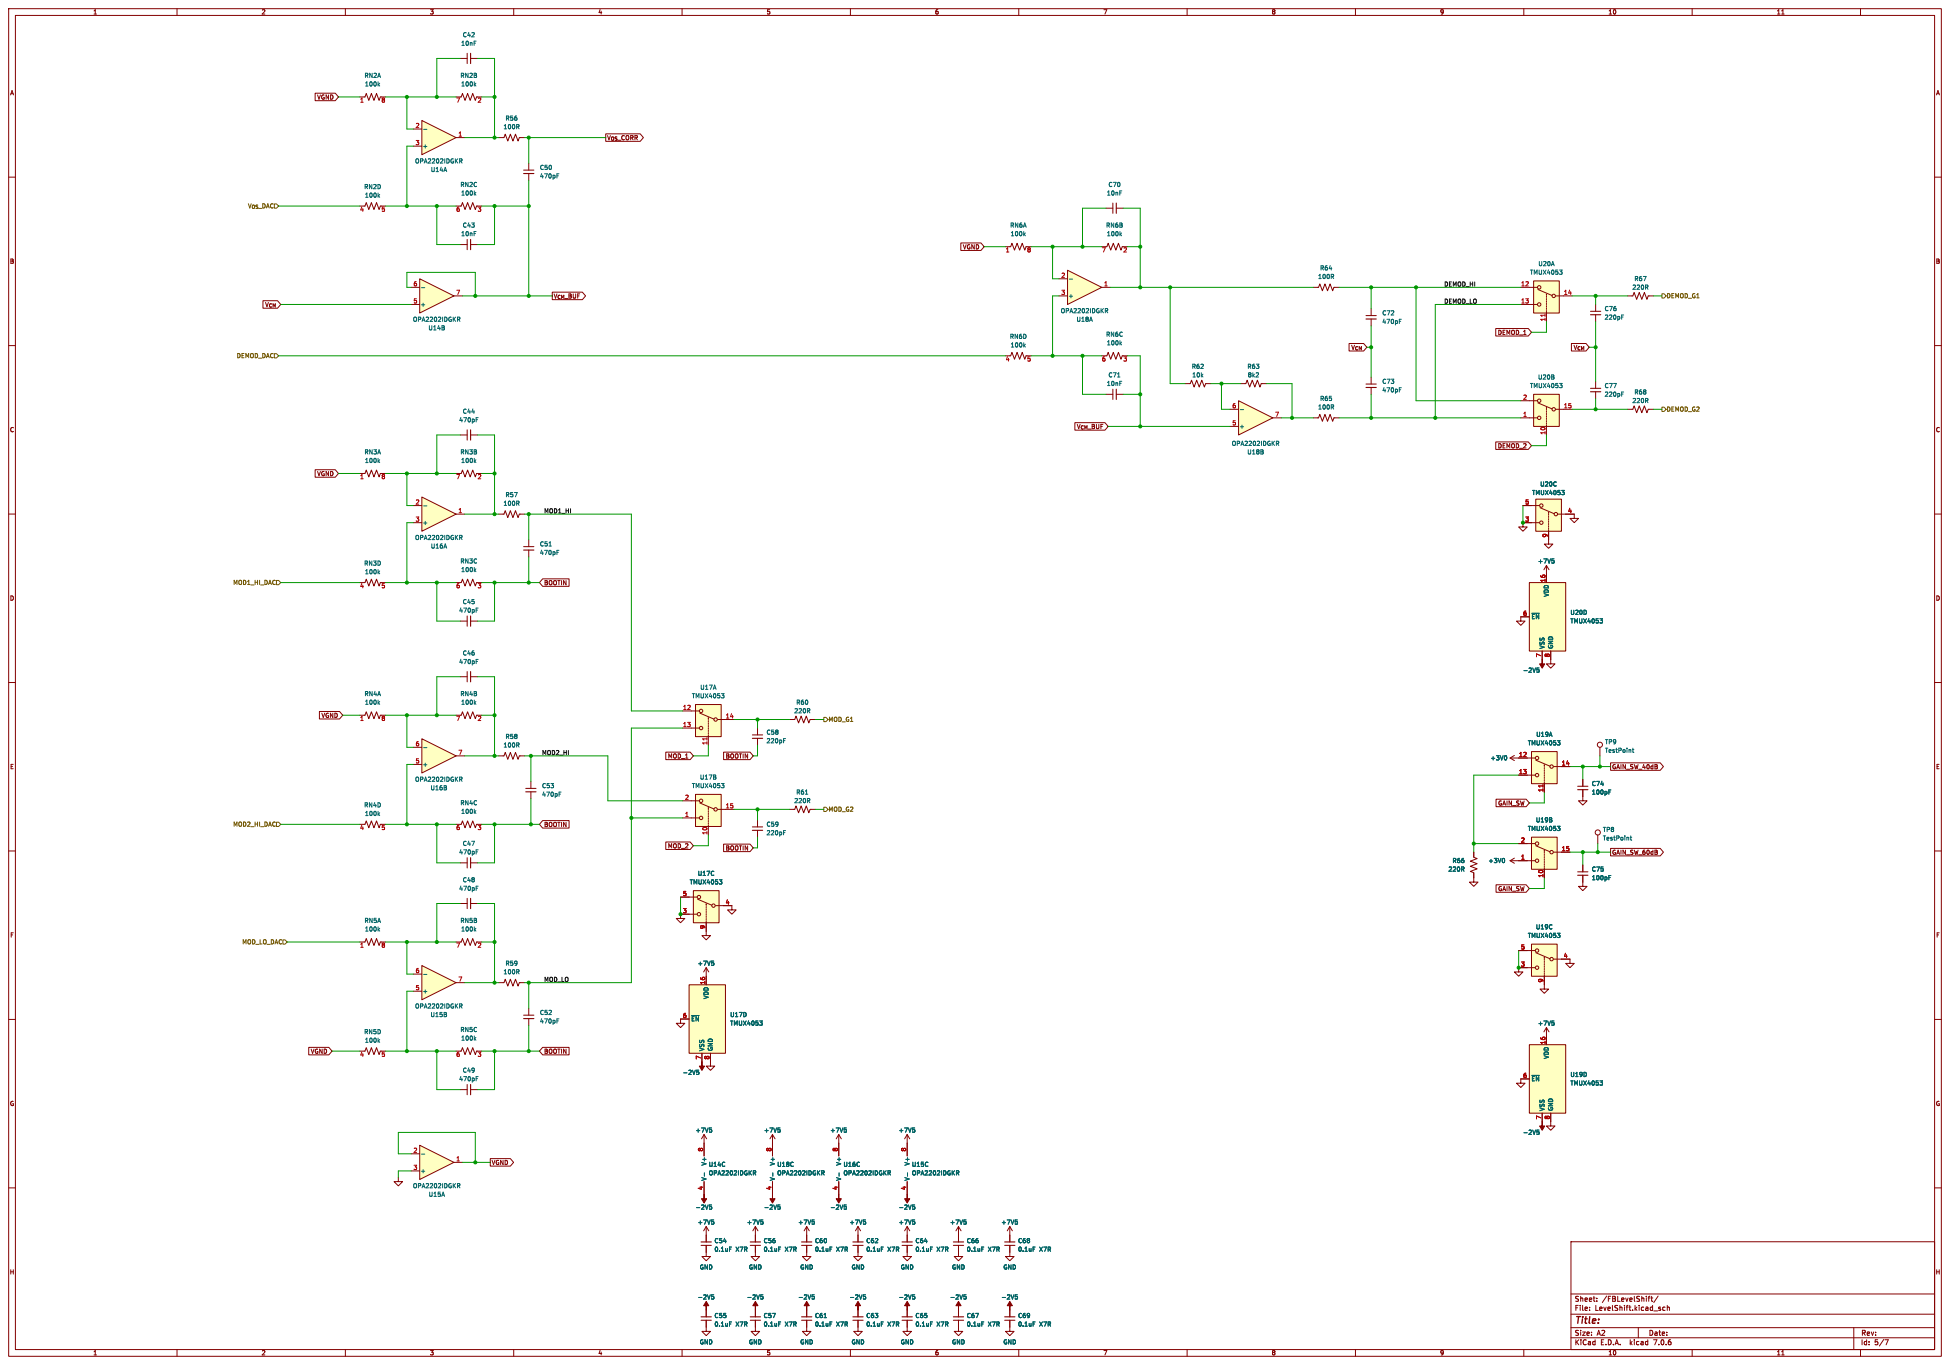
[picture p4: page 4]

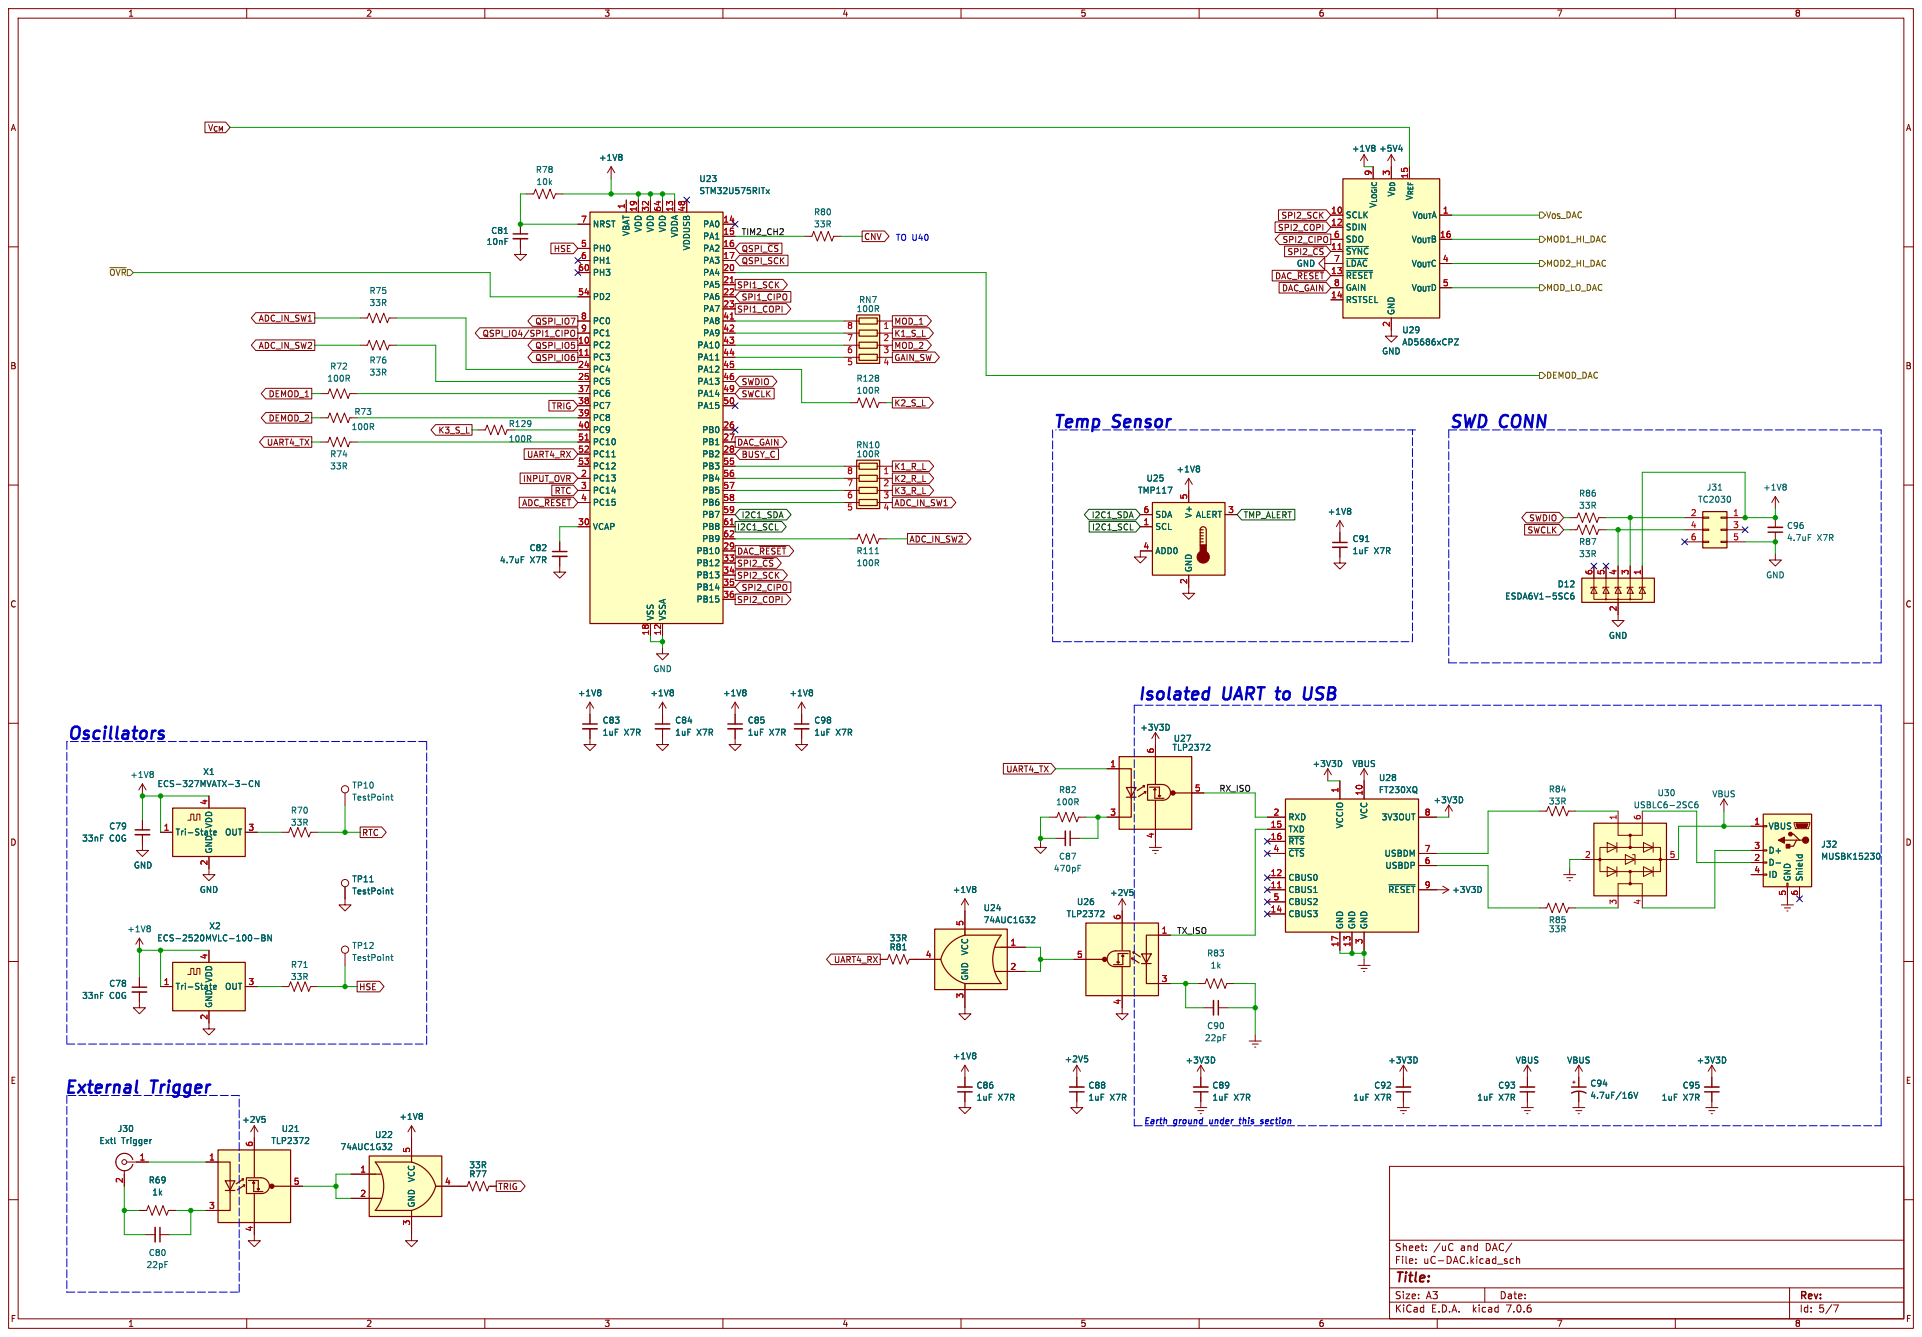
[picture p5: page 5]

2 V_{DD} 3 V_{OUT}C4 V_{OUT}D5 SDO 6 ~{LDAC} 7 GAIN 8 V_{LOGIC} 9 U27 TLP2372

2 V_{DD} 3 V_{OUT}C4 V_{OUT}D5 SDO 6 ~{LDAC} 7 GAIN 8 V_{LOGIC} 9 U29 AD5686xCPZ

1 PC2 10 PC3 11 VSSA 12 VDDA 13 PA0 14 PA1 15 PA2 16 PA3 17 VSS 18 VDD 19 PC13 2 PA4 20 PA5 21 PA6 22 PA7 23 PC4 24 PC5 25 PB0 26 PB1 27 PB2 28 PB10 29 PC14 3 VCAP 30 VDD 32 PB12 33 PB13 34 PB14 35 PB15 36 PC6 37 PC7 38 PC8 39 PC15 4 PC9 40 PA8 41 PA9 42 PA10 43 PA11 44 PA12 45 PA13 46 VDDUSB 48 PA14 49 PH0 5 PA15 50 PC10 51 PC11 52 PC12 53 PD2 54 PB3 55 PB4 56 PB5 57 PB6 58 PB7 59 PH1 6 PH3 60 PB8 61 PB9 62 VDD 64 NRST 7 PC0 8 PC1 9 U23 STM32U575RITx R80
33R GND

1 PC2 10 PC3 11 VSSA 12 VDDA 13 PA0 14 PA1 15 PA2 16 PA3 17 VSS 18 VDD 19 PC13 2 PA4 20 PA5 21 PA6 22 PA7 23 PC4 24 PC5 25 PB0 26 PB1 27 PB2 28 PB10 29 PC14 3 VCAP 30 VDD 32 PB12 33 PB13 34 PB14 35 PB15 36 PC6 37 PC7 38 PC8 39 PC15 4 PC9 40 PA8 41 PA9 42 PA10 43 PA11 44 PA12 45 PA13 46 VDDUSB 48 PA14 49 PH0 5 PA15 50 PC10 51 PC11 52 PC12 53 PD2 54 PB3 55 PB4 56 PB5 57 PB6 58 PB7 59 PH1 6 PH3 60 PB8 61 PB9 62 VDD 64 NRST 7 PC0 8 PC1 9 C82

Isolated UART to USB

1 VCC 10 CBUS1 11 CBUS0 12 GND 13 CBUS3 14 TXD 15 ~{RTS} 16 GND 17 RXD 2 GND

Earth ground under this section External Trigger

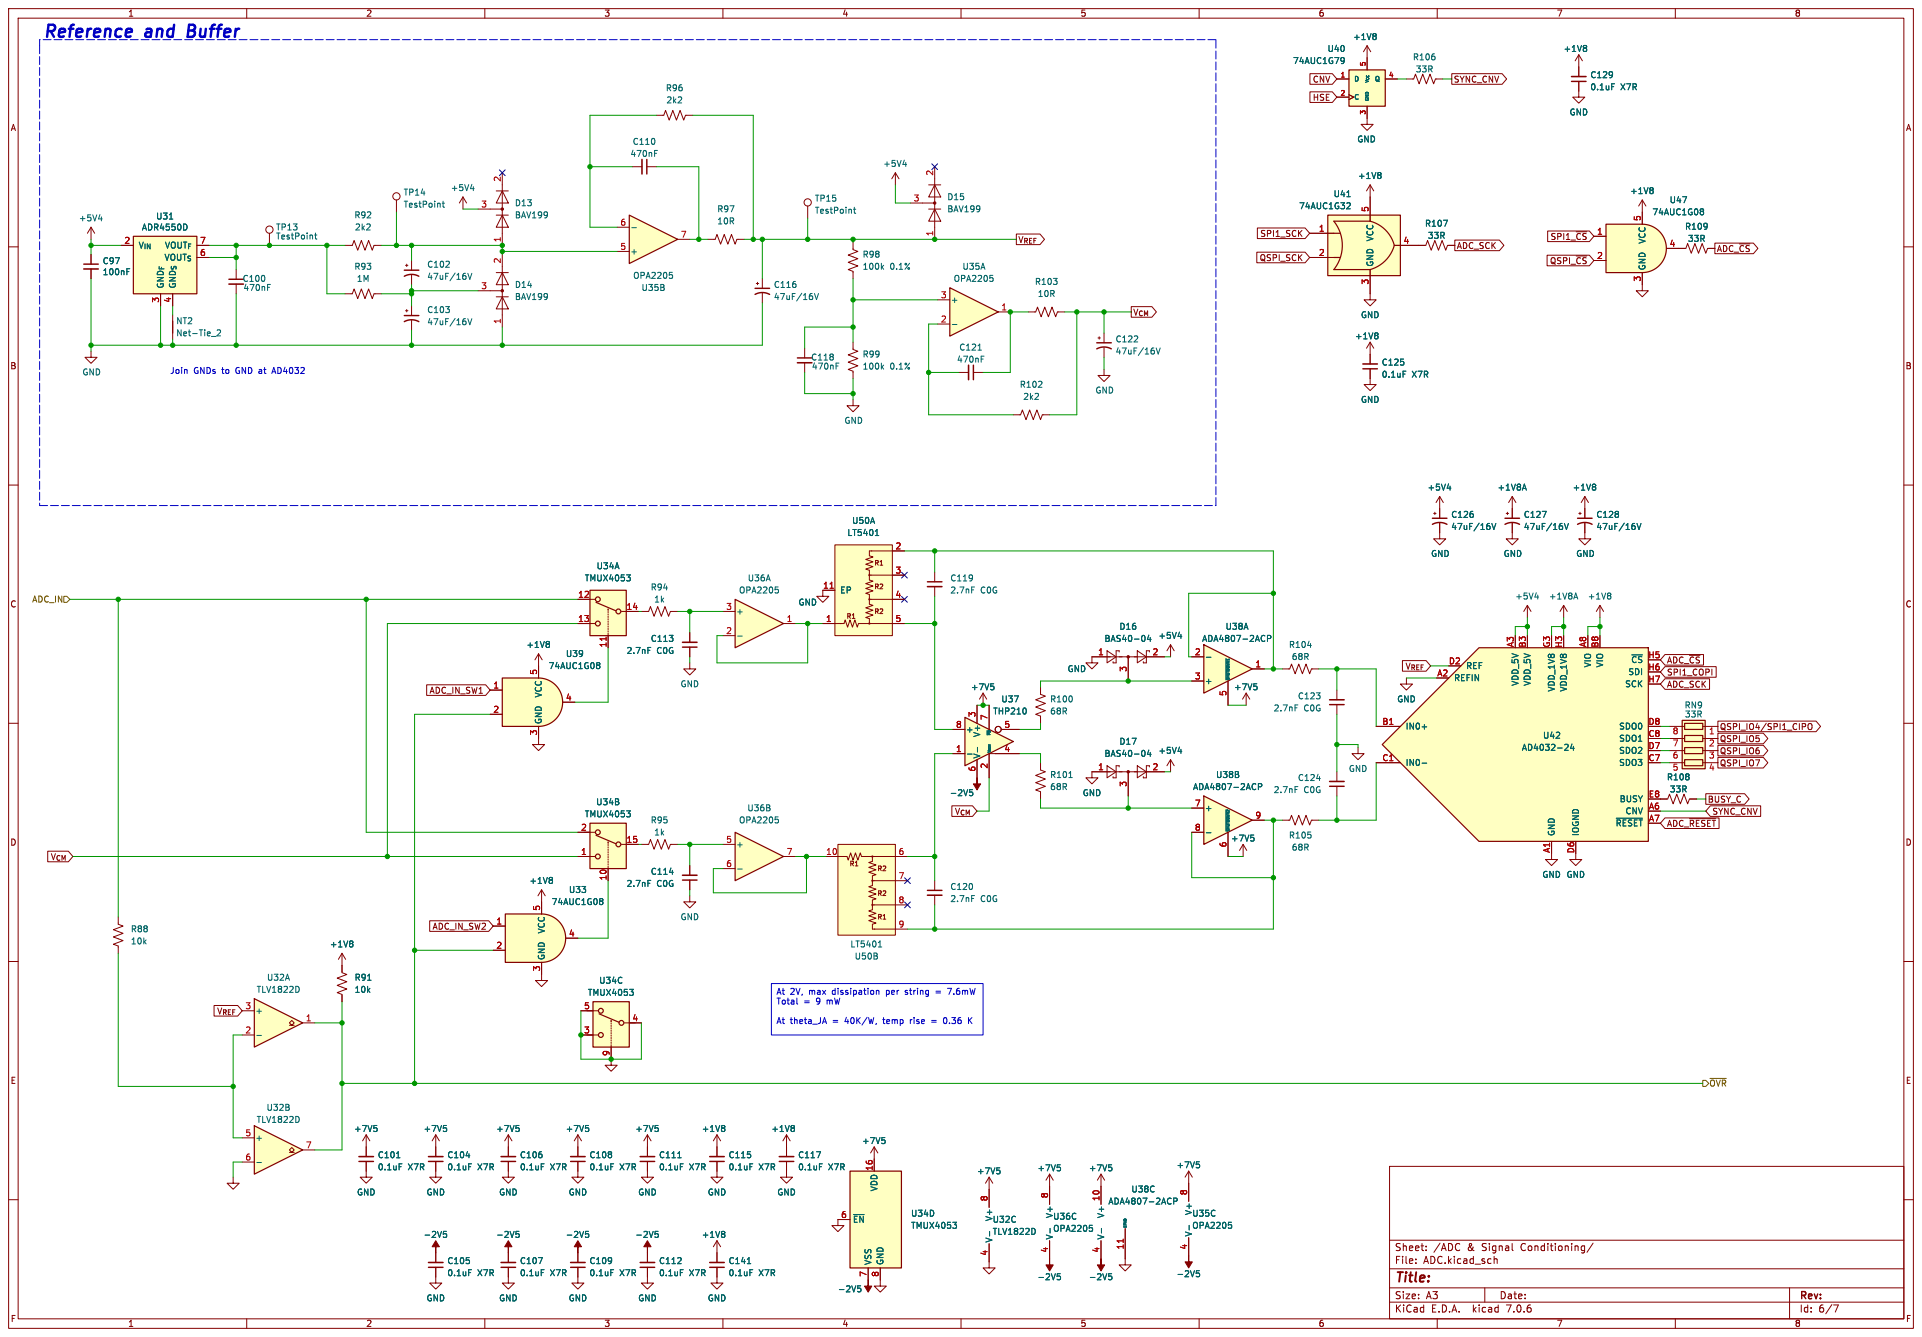
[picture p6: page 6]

Join GNDs to GND at AD4032

~{CS}H5 SDI H6 SCK H7 GND A1 REFIN A2

Id: 6/7 Title: File: ADC.kicad_sch Sheet: /ADC & Signal Conditioning/

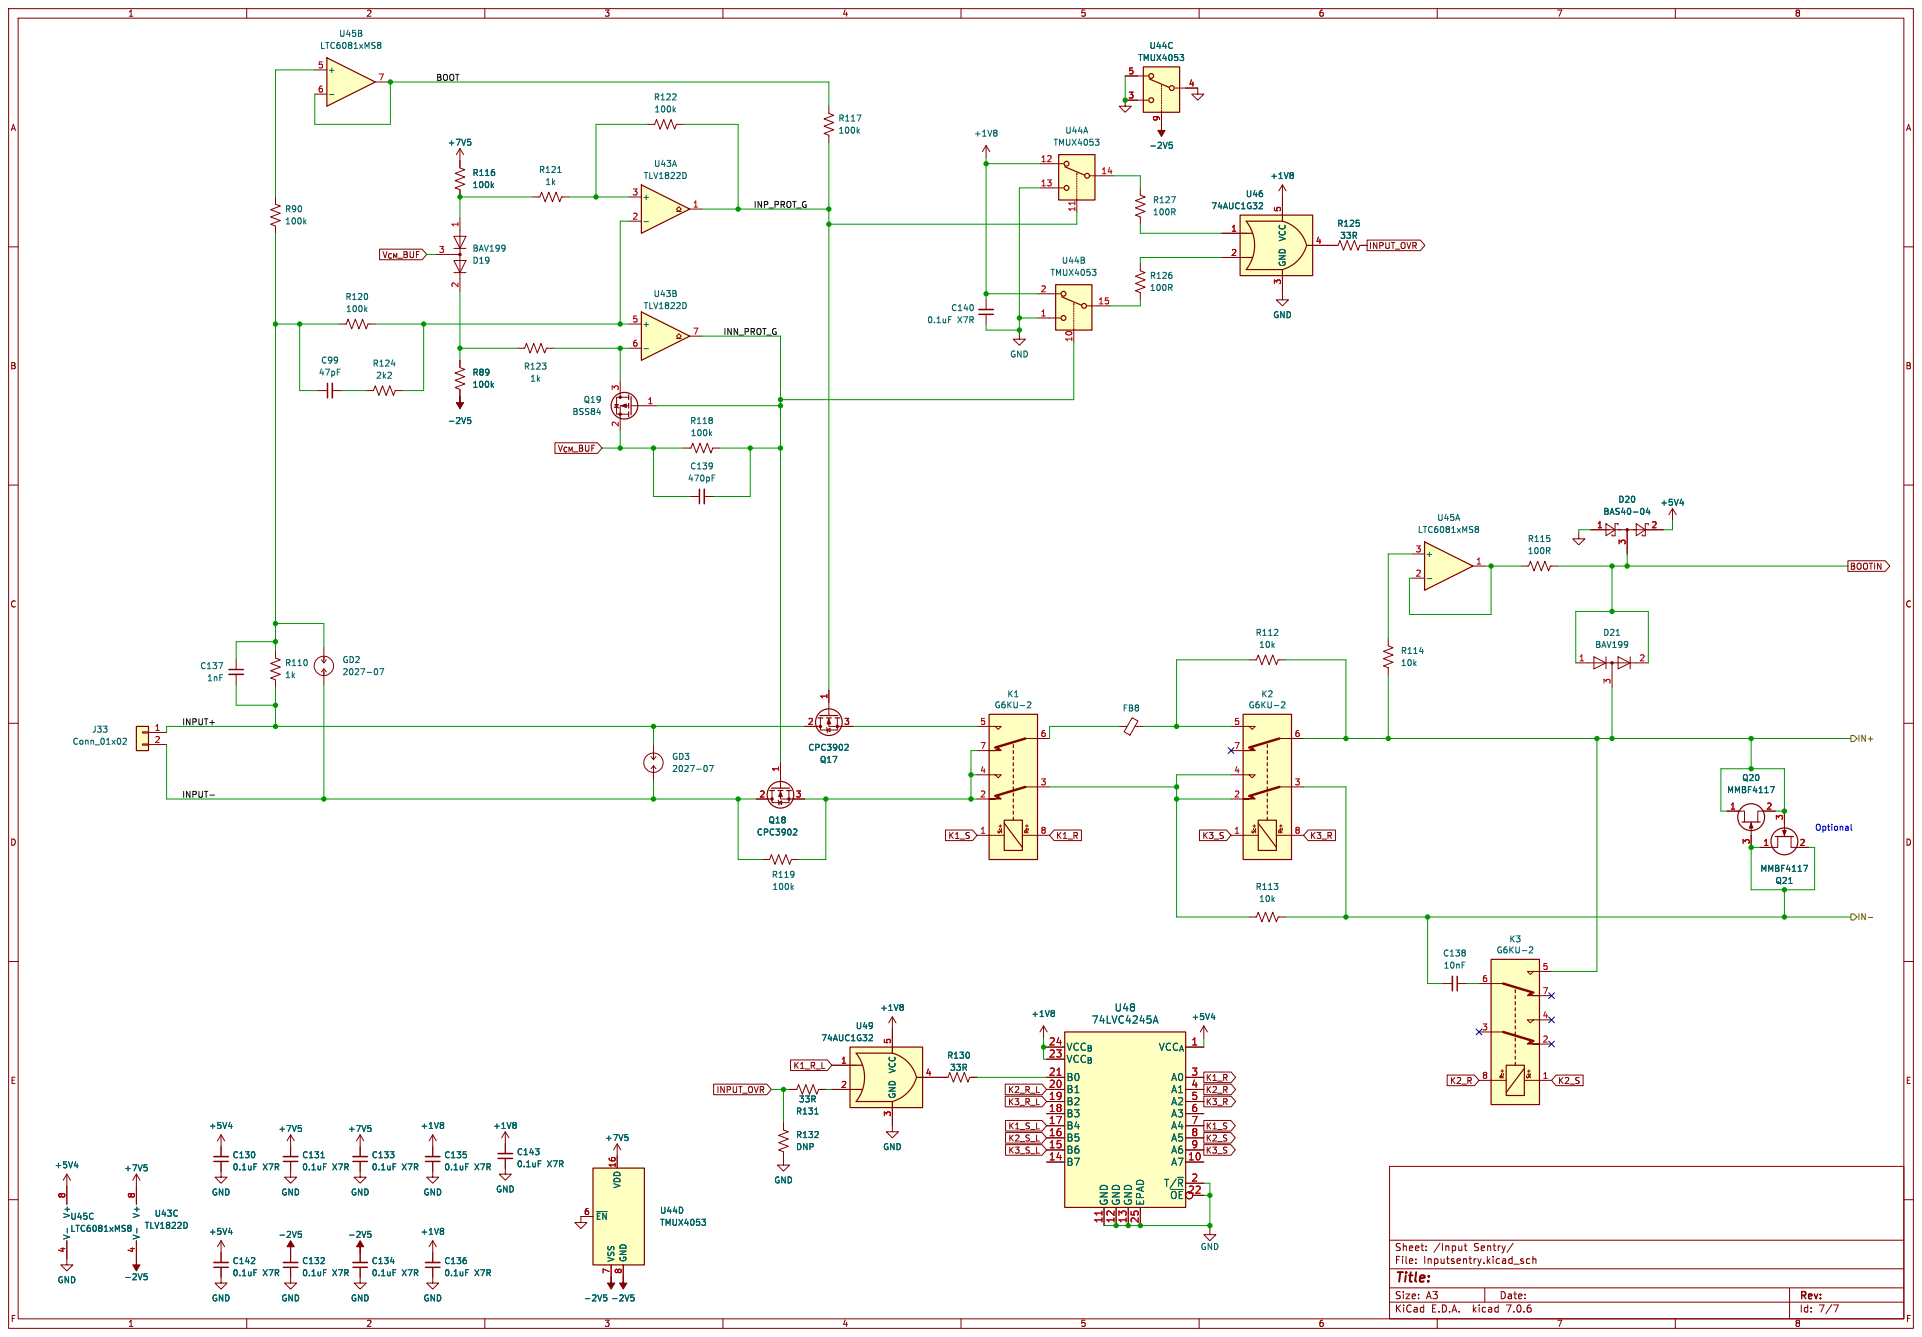
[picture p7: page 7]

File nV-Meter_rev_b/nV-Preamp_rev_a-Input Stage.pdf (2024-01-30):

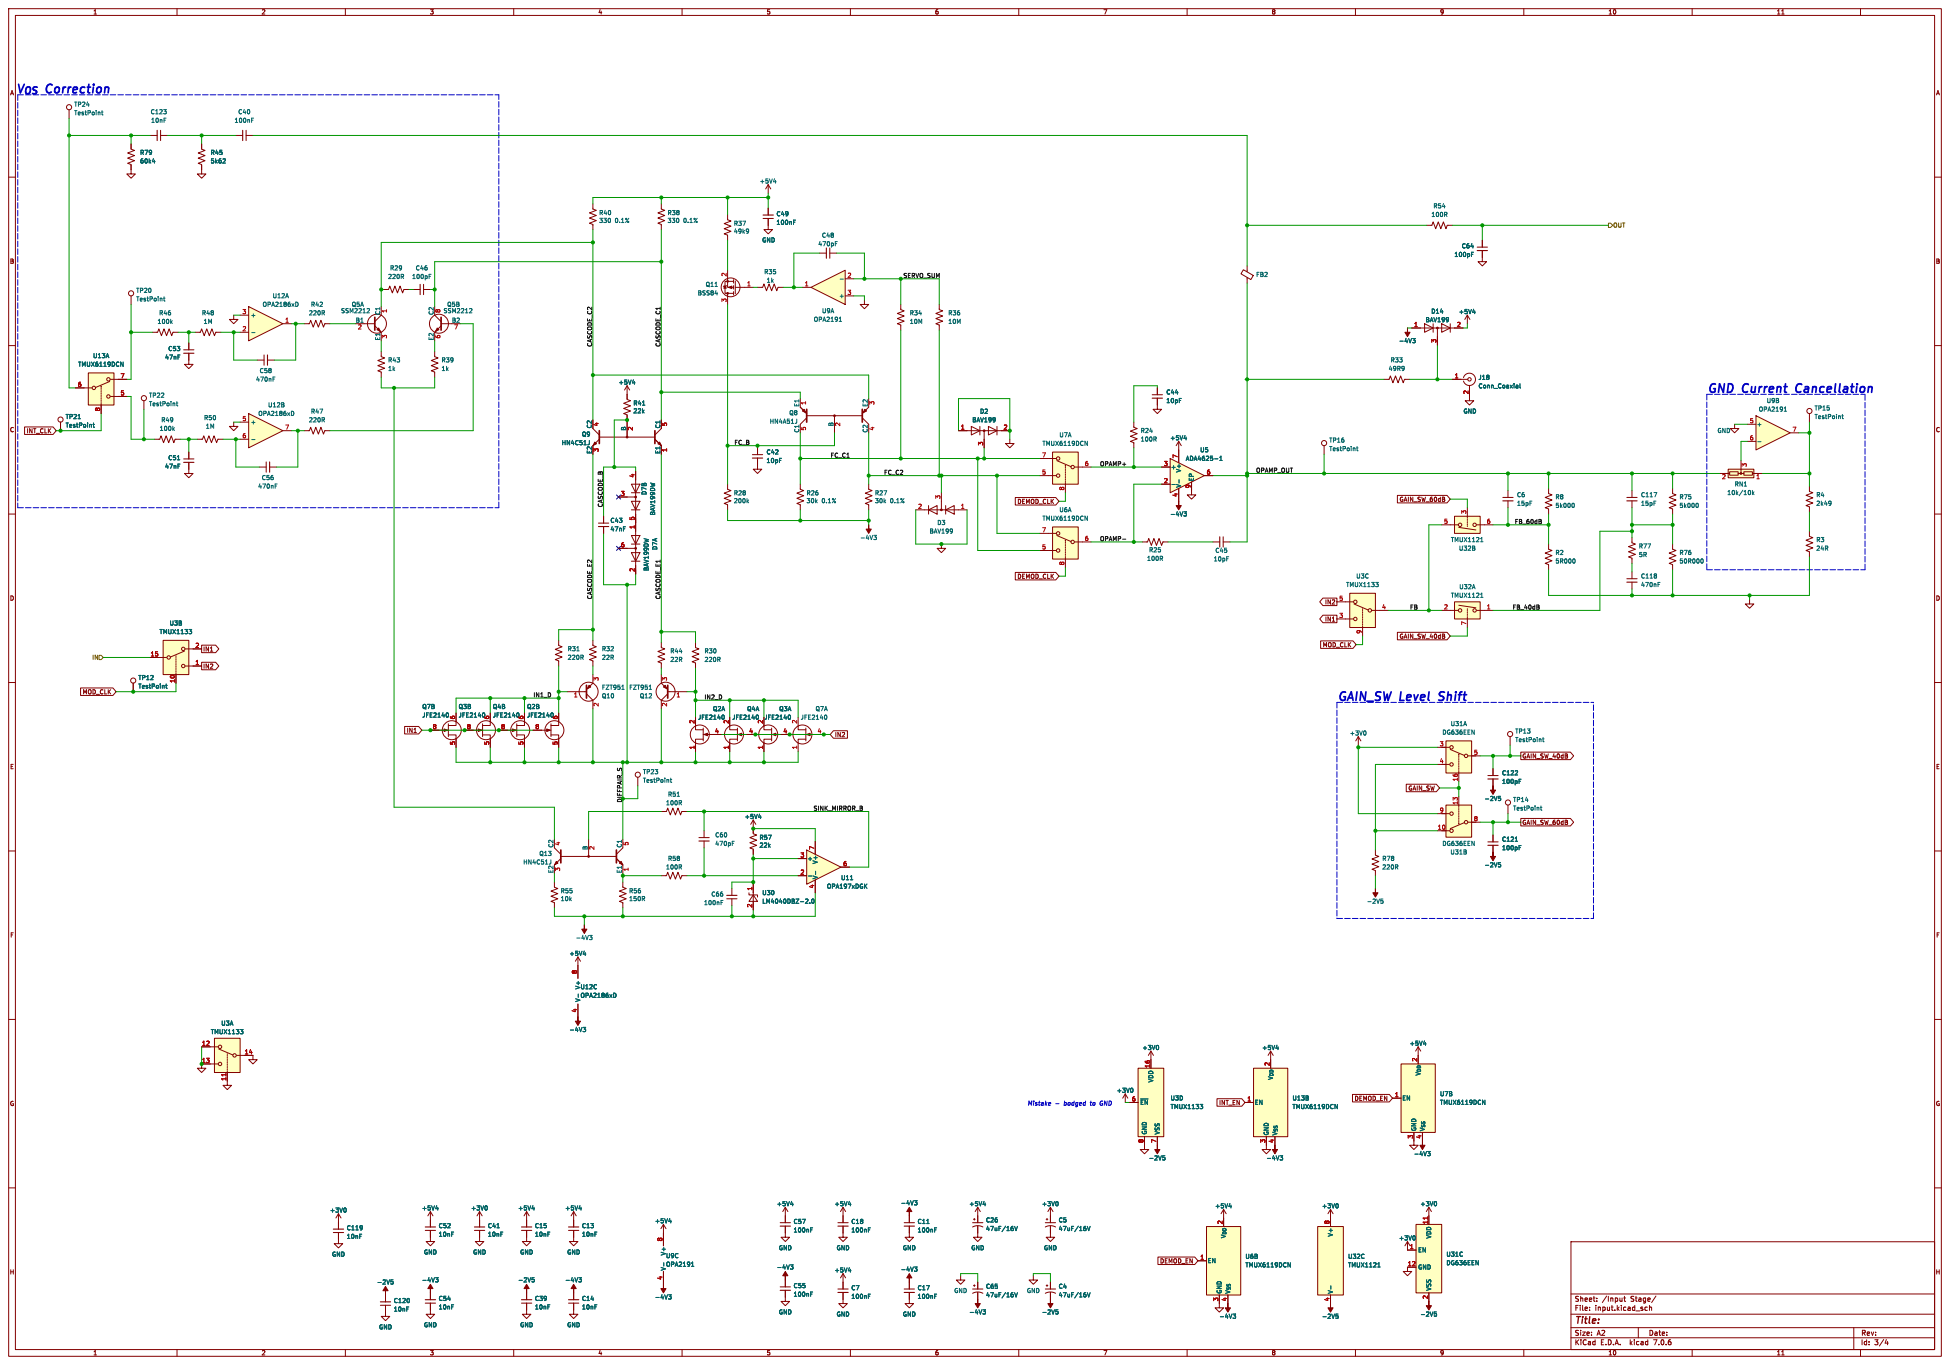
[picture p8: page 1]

GAIN_SW Level Shift Mistake - bodged to GND

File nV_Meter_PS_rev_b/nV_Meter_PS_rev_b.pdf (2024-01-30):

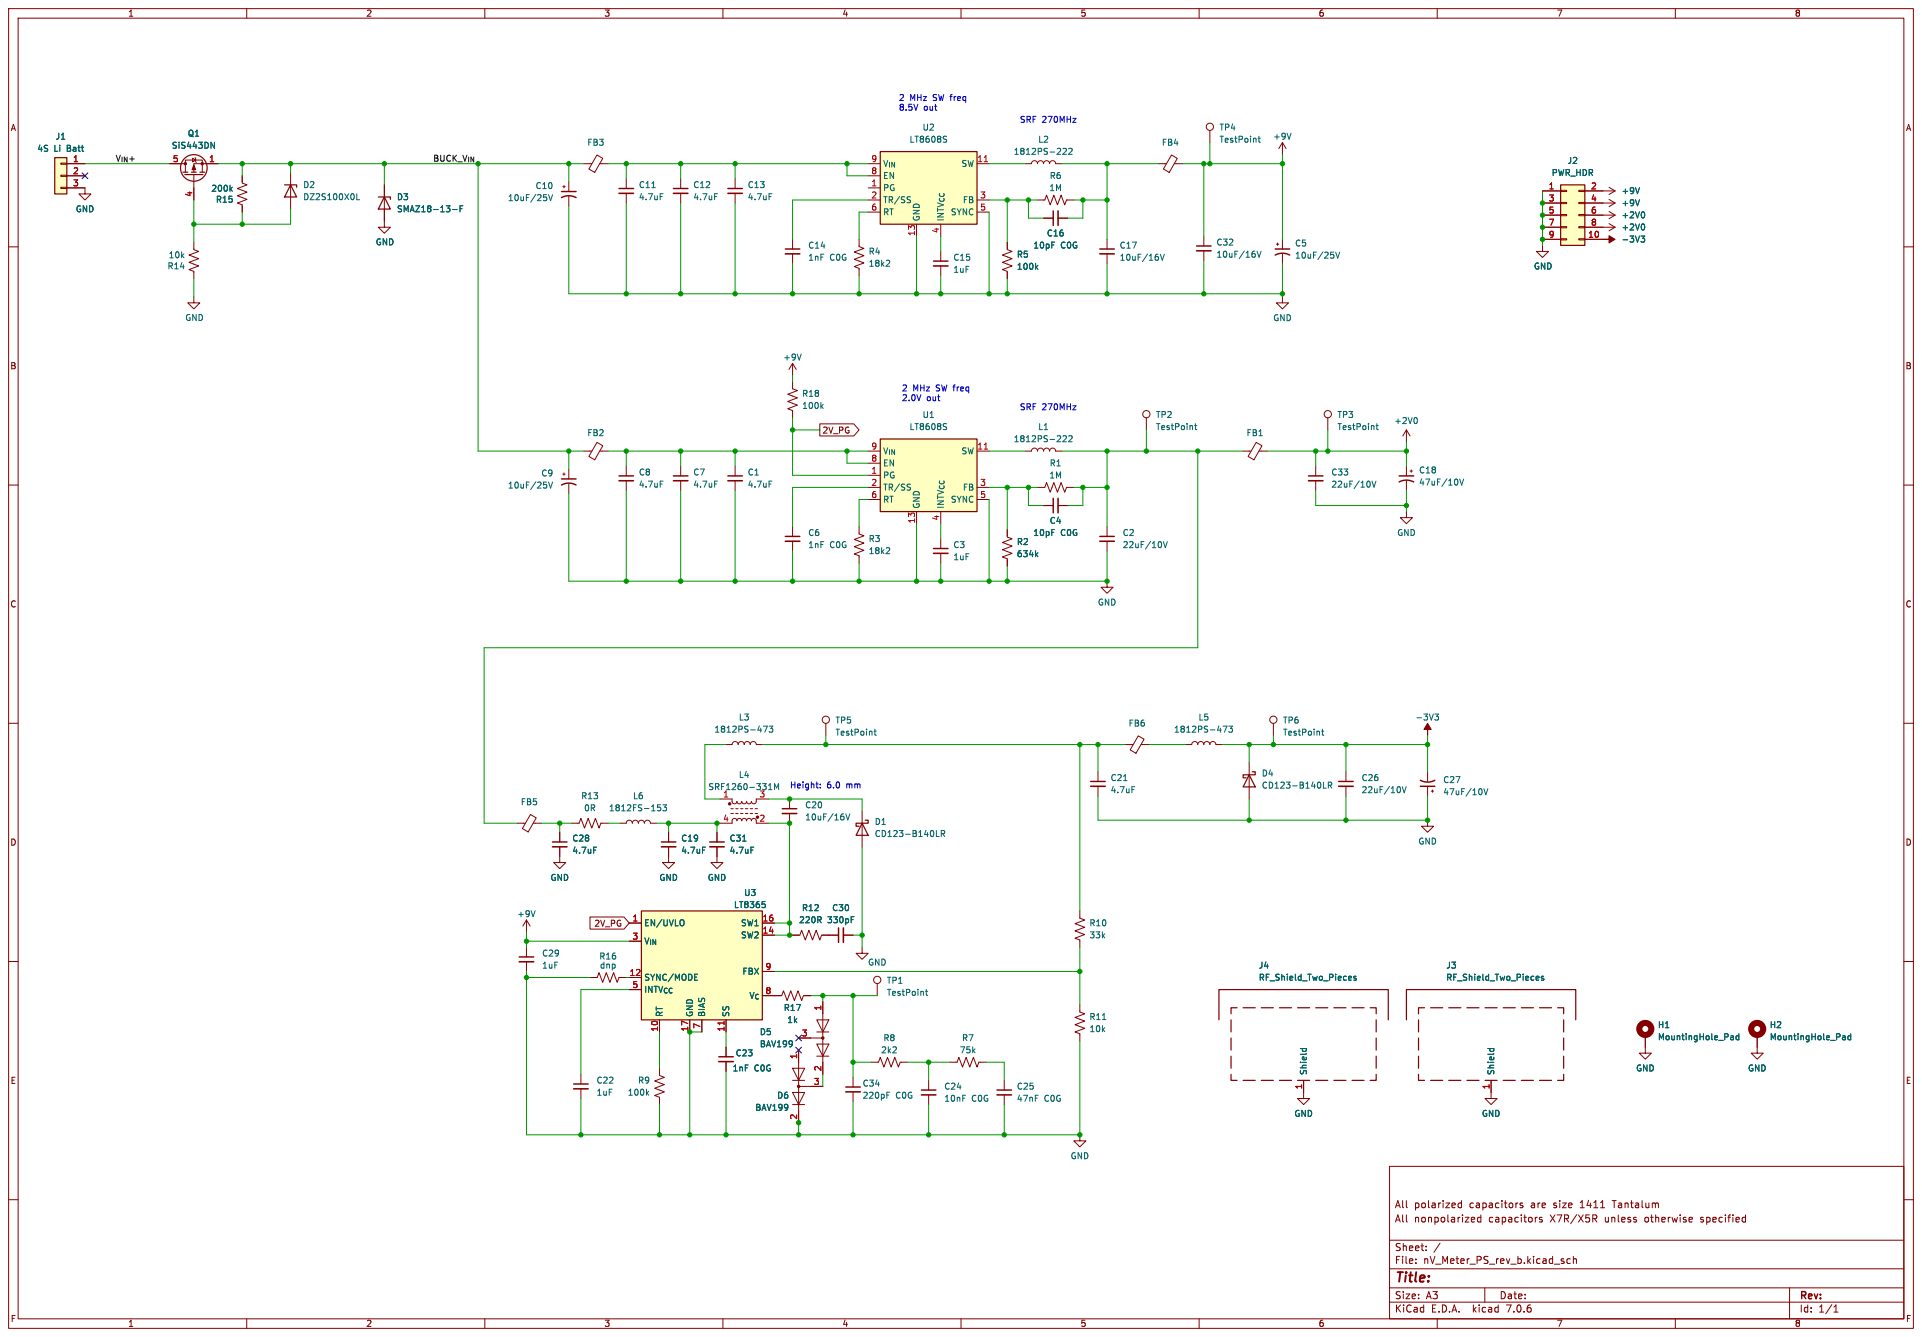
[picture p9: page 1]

SRF 270MHz 2 MHz SW freq

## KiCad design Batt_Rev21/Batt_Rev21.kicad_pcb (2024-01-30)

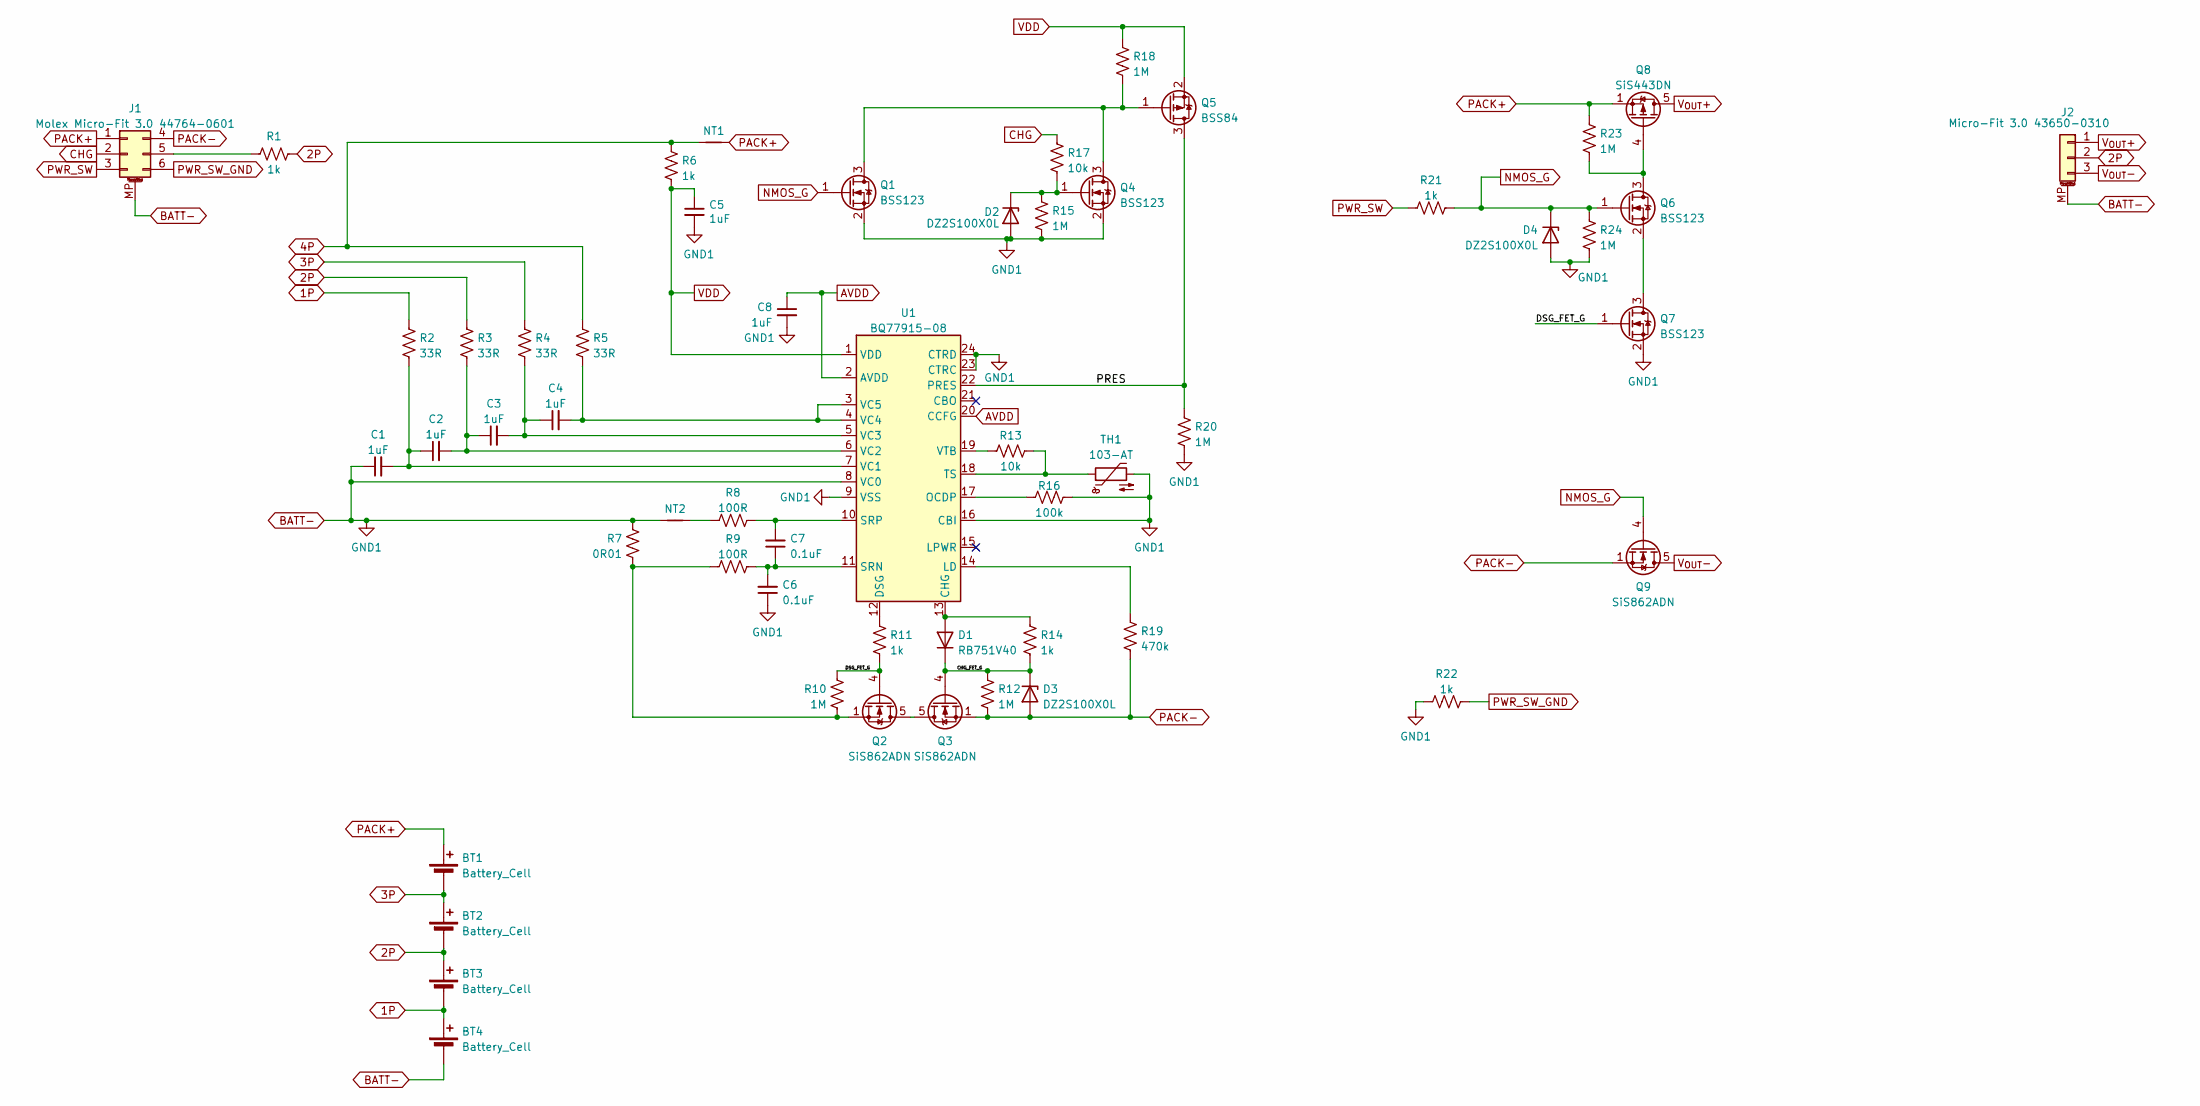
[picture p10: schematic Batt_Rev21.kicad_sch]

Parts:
BT1, BT2, BT3, BT4: Battery_Cell; BatteryHolder_Keystone246_21700
C1, C2, C3, C4, C5, C8: 1uF; C_0603_1608Metric
C6, C7: 0.1uF; C_0603_1608Metric
D1: RB751V40; D_SOD-323
D2, D3, D4: DZ2S100X0L; D_SOD-523
J1: Molex Micro-Fit 3.0 44764-0601; Molex_Micro-Fit_3.0_44764-0601-0600_2x03_P3.00mm_Horizontal
J2: Micro-Fit 3.0 43650-0310; Molex_Micro-Fit_3.0_43650-0310_1x03-1MP_P3.00mm_Horizontal
NT1, NT2: Net-Tie_2; NetTie-2_SMD_Pad0.2mm
Q1, Q4, Q6, Q7: BSS123; SOT-23
Q2, Q3, Q9: SiS862ADN; Vishay_PowerPAK_1212-8_Single
Q5: BSS84; SOT-23
Q8: SiS443DN; Vishay_PowerPAK_1212-8_Single
R1, R6, R11, R14, R21, R22: 1k; R_0603_1608Metric_Outline
R2, R3, R4, R5: 33R; R_0603_1608Metric_Outline
R7: 0R01; R_1206_3216Metric
R8, R9: 100R; R_0603_1608Metric_Outline
R10, R12, R15, R18, R20, R23, R24: 1M; R_0603_1608Metric_Outline
R13, R17: 10k; R_0603_1608Metric_Outline
R16: 100k; R_0603_1608Metric_Outline
R19: 470k; R_0603_1608Metric_Outline
TH1: 103-AT; R_0603_1608Metric_Outline
U1: BQ77915-08; TSSOP-24_4.4x7.8mm_P0.65mm

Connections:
1P: BT3.1 (-), BT4.2 (+), R2.1
2P: BT2.1 (-), BT3.2 (+), J2.2, R1.1, R3.1
3P: BT1.1 (-), BT2.2 (+), R4.1
4P: NT1.2, R5.1, R6.1
/CHG_FET_G: D1.1 (K), D3.1 (K), Q3.4 (G), R12.1, R14.2
/DSG_FET_G: Q2.4 (G), Q7.1 (G), R10.1, R11.2
/PRES: Q5.3 (D), R20.1, U1.22 (PRES)
AVDD: C8.1, U1.2 (AVDD), U1.20 (CCFG)
BATT-: BT4.1 (-), C1.1, C5.2, C6.1, C8.2, D2.2 (A), D4.2 (A), J1.MP (MountPin), J2.MP (MountPin), NT2.2, Q1.2 (S), Q4.2 (S), Q7.2 (S), R7.1, R15.2, R16.1, R20.2, R22.1, R24.2, TH1.2, U1.8 (VC0), U1.9 (VSS), U1.16 (CBI), U1.23 (CTRC), U1.24 (CTRD)
CHG: J1.2, R17.1
NMOS_G: D4.1 (K), Q1.1 (G), Q6.1 (G), Q9.4 (G), R21.2, R24.1
unnamed: D1.2 (A), R14.1, U1.13 (CHG)
unnamed: D2.1 (K), Q4.1 (G), R15.1, R17.2
unnamed: J1.5, R1.2
unnamed: NT2.1, R8.1
unnamed: Q1.3 (D), Q4.3 (D), Q5.1 (G), R18.2
unnamed: Q2.5 (D), Q3.5 (D)
unnamed: Q2.1 (S), Q2.2 (S), Q2.3 (S), R7.2, R9.2, R10.2
unnamed: Q6.3 (D), Q8.4 (G), R23.2
unnamed: Q6.2 (S), Q7.3 (D)
unnamed: R11.1, U1.12 (DSG)
unnamed: R19.1, U1.14 (LD)
unnamed: R16.2, U1.17 (OCDP)
unnamed: C6.2, C7.1, R9.1, U1.11 (SRN)
unnamed: C7.2, R8.2, U1.10 (SRP)
unnamed: R13.1, TH1.1, U1.18 (TS)
unnamed: C1.2, C2.1, R2.2, U1.7 (VC1)
unnamed: C2.2, C3.1, R3.2, U1.6 (VC2)
unnamed: C3.2, C4.1, R4.2, U1.5 (VC3)
unnamed: C4.2, R5.2, U1.3 (VC5), U1.4 (VC4)
unnamed: R13.2, U1.19 (VTB)
PACK+: BT1.2 (+), J1.1, NT1.1, Q8.1 (S), Q8.2 (S), Q8.3 (S), R23.1
PACK-: D3.2 (A), J1.4, Q3.1 (S), Q3.2 (S), Q3.3 (S), Q9.1 (S), Q9.2 (S), Q9.3 (S), R12.2, R19.2
PWR_SW: J1.3, R21.1
PWR_SW_GND: J1.6, R22.2
VDD: C5.1, Q5.2 (S), R6.2, R18.1, U1.1 (VDD)
V_{OUT}+: J2.1, Q8.5 (D)
V_{OUT}-: J2.3, Q9.5 (D)

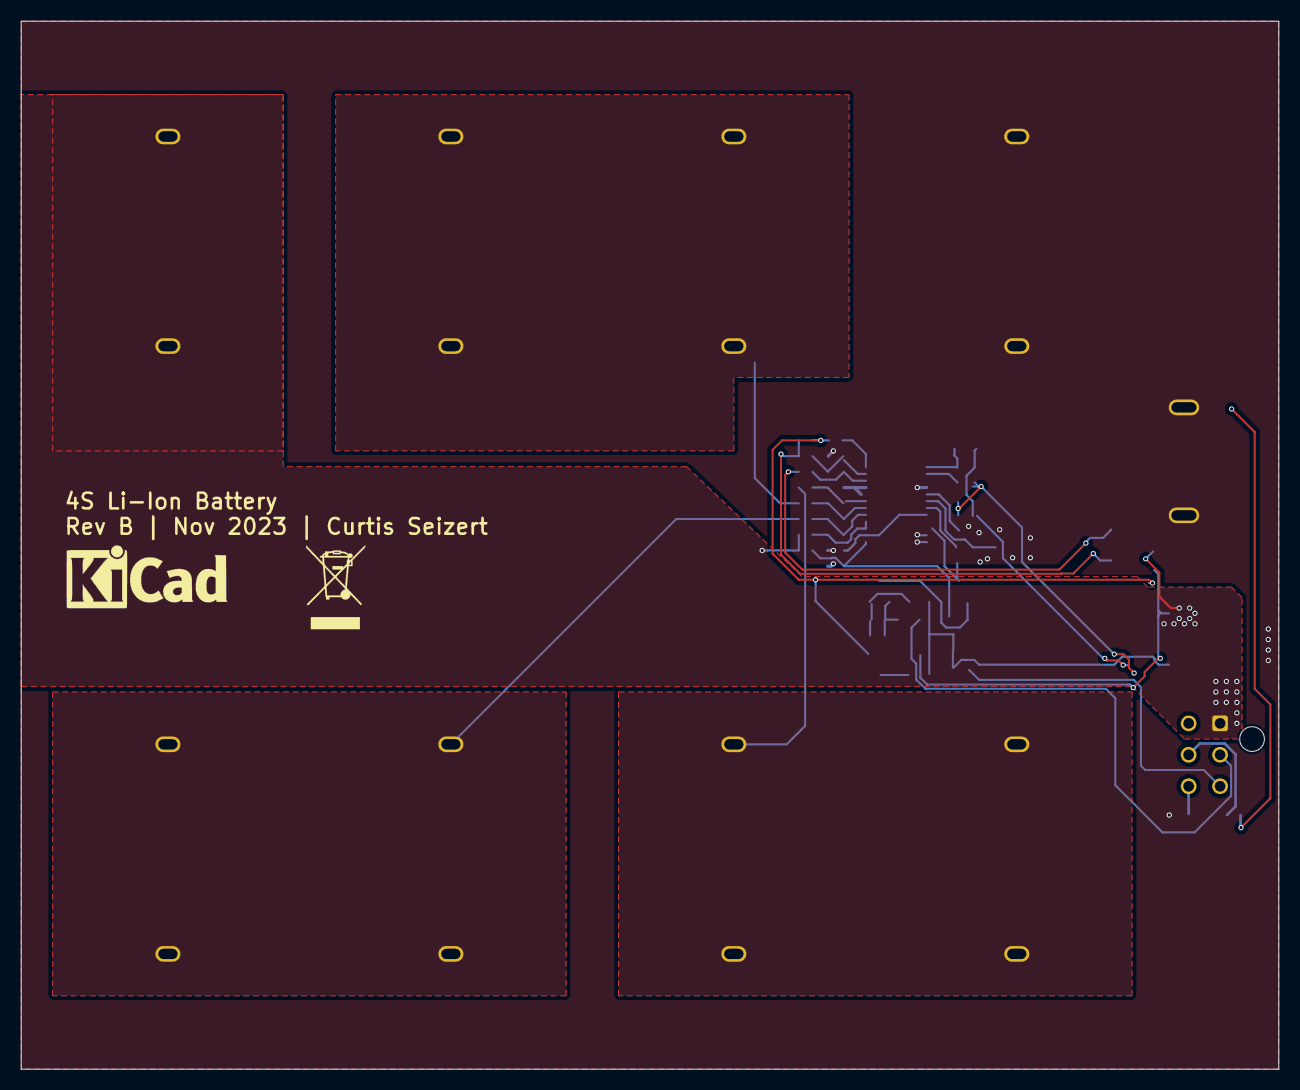
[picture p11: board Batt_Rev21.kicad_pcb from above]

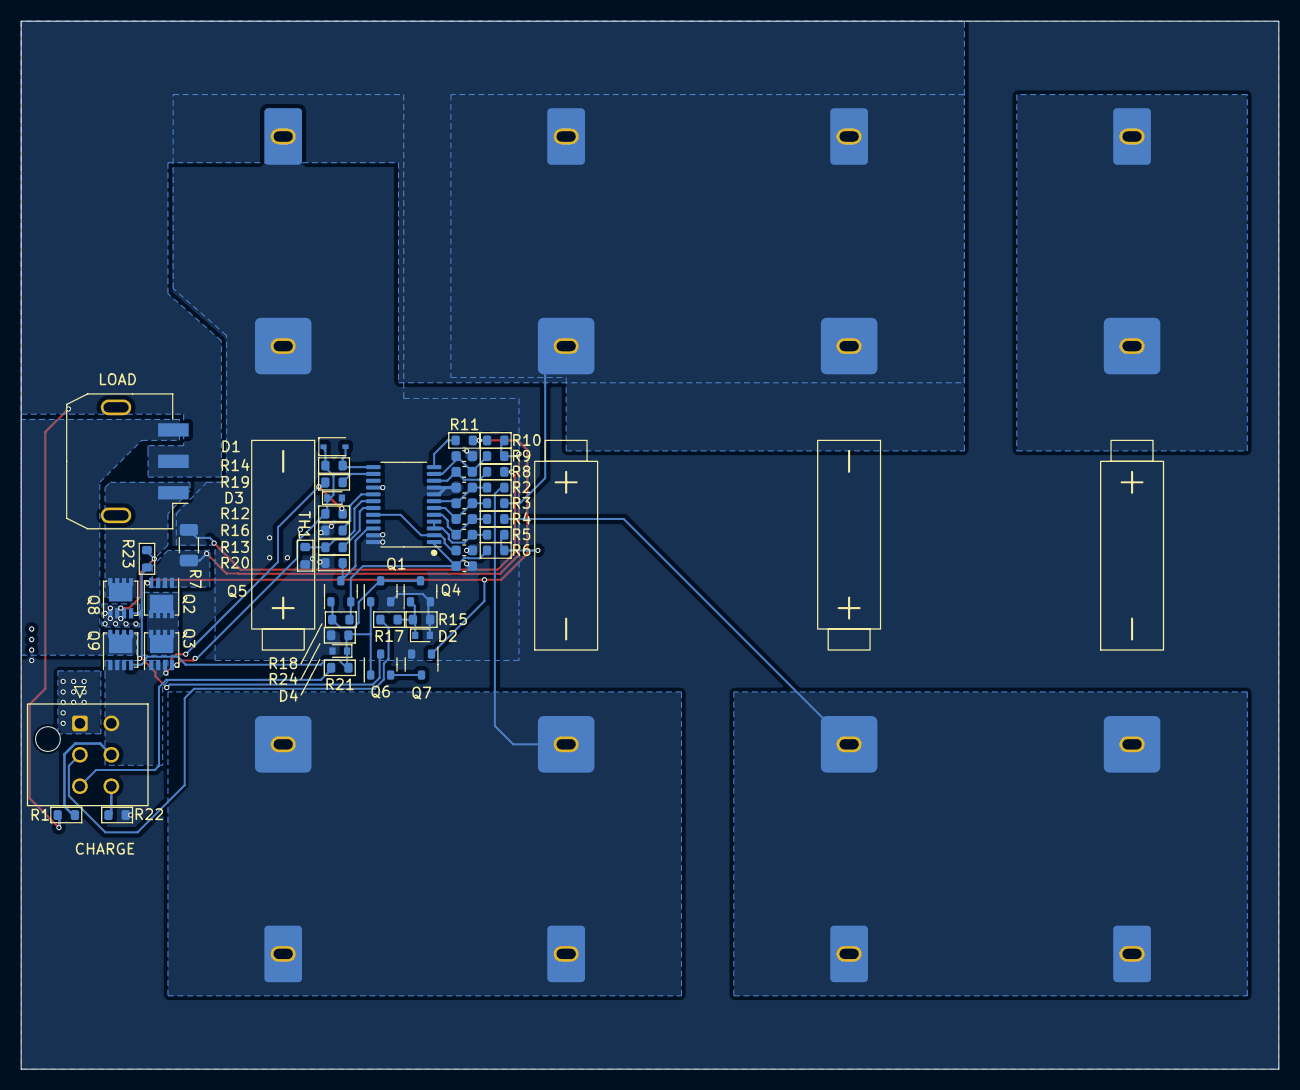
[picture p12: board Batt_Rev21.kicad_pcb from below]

Board: 2 copper layers, 120.0 x 100.0 mm, 55 parts (55 on the bottom side), 38 nets.

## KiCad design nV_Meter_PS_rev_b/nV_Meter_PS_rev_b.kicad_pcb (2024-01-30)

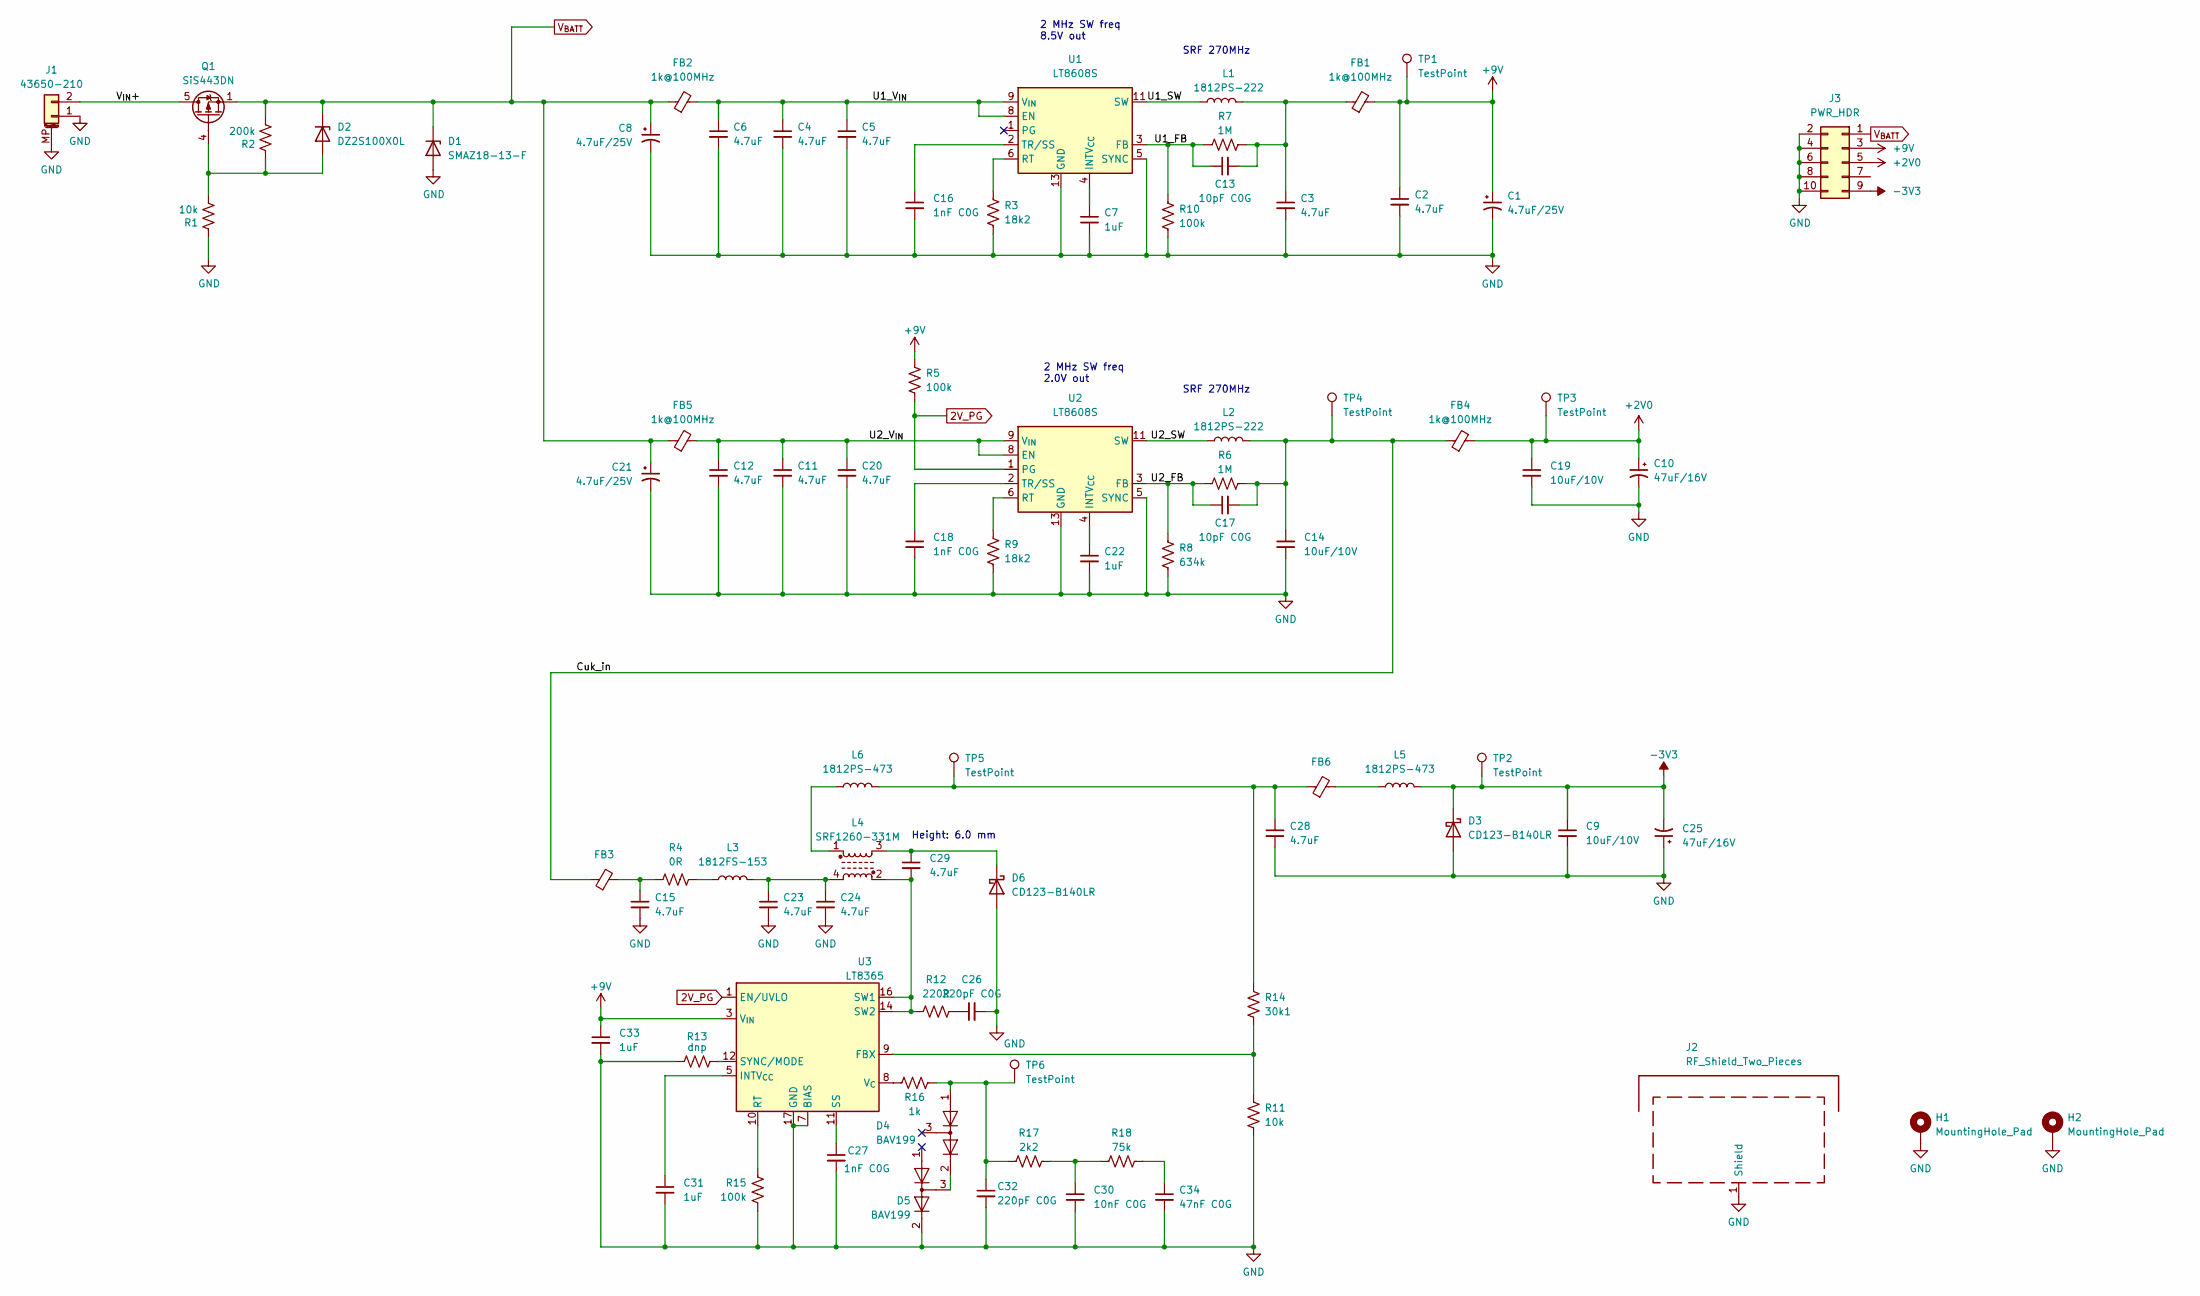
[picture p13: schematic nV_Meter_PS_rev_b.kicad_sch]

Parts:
C1, C8, C21: 4.7uF/25V; CP_EIA-3528-12_Kemet-T; Part Number x
C2, C3, C4, C5, C6, C11, C12, C15, C20, C23, C24, C28, C29: 4.7uF; C_0805_2012Metric; Part Number GRM21BZ7YA475KE15K
C7, C22, C31, C33: 1uF; C_0402_1005Metric; Part Number GRM155R61H105KE05D
C9, C14, C19: 10uF/10V; C_0805_2012Metric; Part Number x
C10, C25: 47uF/16V; CP_EIA-3528-12_AVX_B_Conformal; Part Number F951C476MBAAQ2
C13, C17: 10pF C0G; C_0402_1005Metric; Part Number GRM1555C1H100JA01D
C16, C18, C27: 1nF C0G; C_0402_1005Metric; Part Number GRM1555C1H102JA01J
C26, C32: 220pF C0G; C_0402_1005Metric; Part Number GRM1555C1H221JA01J
C30: 10nF C0G; C_0402_1005Metric; Part Number x
C34: 47nF C0G; C_0805_2012Metric; Part Number x
D1: SMAZ18-13-F; D_SOD-123F; Part Number HPZR-C18-QX
D2: DZ2S100X0L; D_SOD-523; Part Number x
D3, D6: CD123-B140LR; D_PowerDI-123; Part Number CD123-B140LR
D4, D5: BAV199; SOT-23; Part Number x
FB1, FB2, FB3, FB4, FB5, FB6: 1k@100MHz; L_1206_3216Metric; Part Number HZ1206D102R-10
H1, H2: MountingHole_Pad; MountingHole_2.2mm_M2_Pad_Via
J1: 43650-210; Molex_Micro-Fit_3.0_43650-0210_1x02-1MP_P3.00mm_Horizontal
J2: RF_Shield_Two_Pieces; Orbel_L-1750TB2250
J3: PWR_HDR; PinHeader_2x05_P2.54mm_Vertical
L1, L2: 1812PS-222; L_1812_4532Metric
L3: 1812FS-153; L_1812_4532Metric
L4: SRF1260-331M; L_Bourns_SRF1260
L5, L6: 1812PS-473; L_1812_4532Metric
Q1: SiS443DN; Vishay_PowerPAK_1212-8_Single
R1, R11: 10k; R_0402_1005Metric; Part Number RT0402FRE0710KL
R2: 200k; R_0402_1005Metric; Part Number MCS04020C2003FE000
R3, R9: 18k2; R_0402_1005Metric; Part Number RC0402FR-1318K2L
R4: 0R; R_1206_3216Metric_red; Part Number x
R5, R10, R15: 100k; R_0402_1005Metric; Part Number RT0402FRE07100KL
R6, R7: 1M; R_0402_1005Metric; Part Number RC0402FR-7W1ML
R8: 634k; R_0402_1005Metric; Part Number RC0402FR-07634KL
R12: 220R; R_0402_1005Metric; Part Number RC0402JR-7D220RL
R13: dnp; R_0402_1005Metric; Part Number x
R14: 30k1; R_0402_1005Metric; Part Number RR0510P-3012-D
R16: 1k; R_0402_1005Metric; Part Number RR0510P-102-D
R17: 2k2; R_0402_1005Metric; Part Number RC0402JR-072K2L
R18: 75k; R_0402_1005Metric; Part Number RC0402JR-0775KL
TP1, TP2, TP3, TP4, TP5, TP6: TestPoint; TestPoint_Pad_D1.0mm
U1, U2: LT8608S; Linear_LQFN12_2x3mm_0.5x1.45mmEP
U3: LT8365; MSOP-12-16-1EP_3x4mm_P0.5mm_EP1.65x2.85mm

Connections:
2V_PG: R5.1, U2.1 (PG), U3.1 (EN/UVLO)
+2V0: C10.1, C19.1, FB4.2, J3.5, TP3.1
+9V: C1.1, C2.1, C33.1, FB1.2, J3.3, R5.2, TP1.1, U3.3 (V_{IN})
-3V3: C9.1, C25.2, D3.1 (K), J3.9, L5.2, TP2.1
/Cuk_in: C14.1, C17.2, FB3.1, FB4.1, L2.2, R6.2, TP4.1
/U1_FB: C13.1, R7.1, R10.2, U1.3 (FB)
/U1_SW: L1.1, U1.11 (SW), U1.12 (SW)
/U1_V_{IN}: C4.1, C5.1, C6.1, FB2.2, U1.8 (EN), U1.9 (V_{IN}), U1.10 (V_{IN})
/U2_FB: C17.1, R6.1, R8.2, U2.3 (FB)
/U2_SW: L2.1, U2.11 (SW), U2.12 (SW)
/U2_V_{IN}: C11.1, C12.1, C20.1, FB5.2, U2.8 (EN), U2.9 (V_{IN}), U2.10 (V_{IN})
/V_{IN}+: J1.2, Q1.5 (D)
GND: C1.2, C2.2, C3.2, C4.2, C5.2, C6.2, C7.2, C8.2, C9.2, C10.2, C11.2, C12.2, C14.2, C15.2, C16.2, C18.2, C19.2, C20.2, C21.2, C22.2, C23.2, C24.2, C25.1, C26.2, C27.2, C28.2, C30.2, C31.2, C32.2, C33.2, C34.2, D1.2 (A), D3.2 (A), D5.2 (A), D6.2 (A), H1.1, H2.1, J1.1, J1.MP (MountPin), J2.1 (Shield), J3.2, J3.4, J3.6, J3.8, J3.10, R1.1, R3.1, R8.1, R9.1, R10.1, R11.1, R13.2, R15.1, U1.5 (SYNC), U1.7 (GND), U1.13 (GND), U2.5 (SYNC), U2.7 (GND), U2.13 (GND), U3.7 (BIAS), U3.17 (GND)
unnamed: C3.1, C13.2, FB1.1, L1.2, R7.2
unnamed: C15.1, FB3.2, R4.2
unnamed: C23.1, C24.1, L3.2, L4.4
unnamed: C26.1, R12.1
unnamed: C28.1, FB6.1, L6.2, R14.2, TP5.1
unnamed: C30.1, R17.1, R18.2
unnamed: C32.1, D4.1 (K), R16.2, R17.2, TP6.1
unnamed: C34.1, R18.1
unnamed: D2.2 (A), Q1.4 (G), R1.2, R2.1
unnamed: D4.2 (A), D5.3 (K)
unnamed: C29.1, D6.1 (K), L4.3
unnamed: FB6.2, L5.1
unnamed: L3.1, R4.1
unnamed: L4.1, L6.1
unnamed: C7.1, U1.4 (INTV_{CC})
unnamed: R3.2, U1.6 (RT)
unnamed: C16.1, U1.2 (TR/SS)
unnamed: C22.1, U2.4 (INTV_{CC})
unnamed: R9.2, U2.6 (RT)
unnamed: C18.1, U2.2 (TR/SS)
unnamed: R11.2, R14.1, U3.9 (FBX)
unnamed: C31.1, U3.5 (INTV_{CC})
unnamed: R15.2, U3.10 (RT)
unnamed: C27.1, U3.11 (SS)
unnamed: C29.2, L4.2, R12.2, U3.14 (SW2), U3.16 (SW1)
unnamed: R13.1, U3.12 (SYNC/MODE)
unnamed: R16.1, U3.8 (V_{C})
V_{BATT}: C8.1, C21.1, D1.1 (K), D2.1 (K), FB2.1, FB5.1, J3.1, Q1.1 (S), Q1.2 (S), Q1.3 (S), R2.2

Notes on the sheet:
Height: 6.0 mm
SRF 270MHz
2 MHz SW freq 8.5V out
2 MHz SW freq 2.0V out

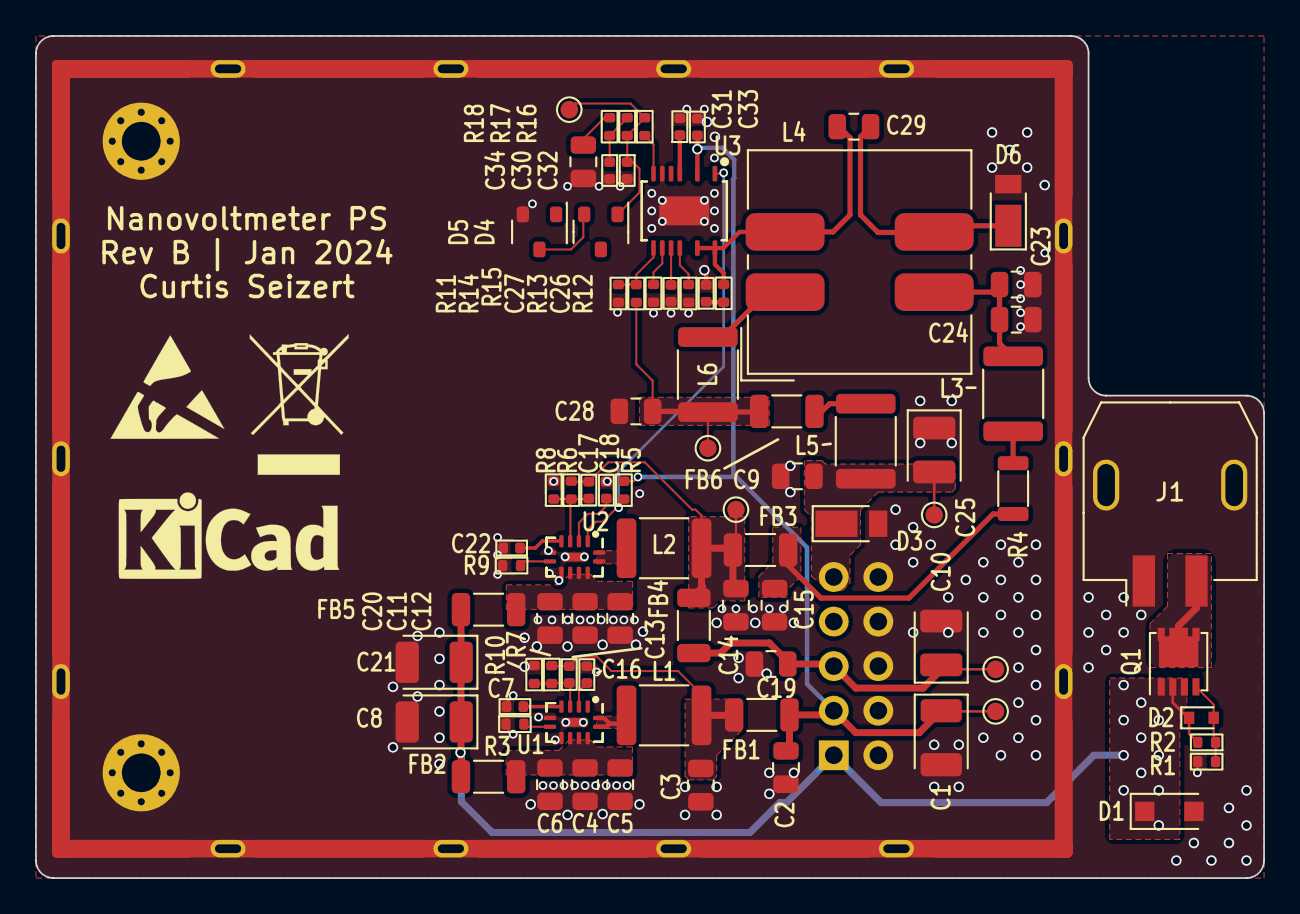
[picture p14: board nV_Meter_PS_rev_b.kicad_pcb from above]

Board: 4 copper layers, 70.0 x 48.0 mm, 85 parts (1 on the bottom side), 41 nets.

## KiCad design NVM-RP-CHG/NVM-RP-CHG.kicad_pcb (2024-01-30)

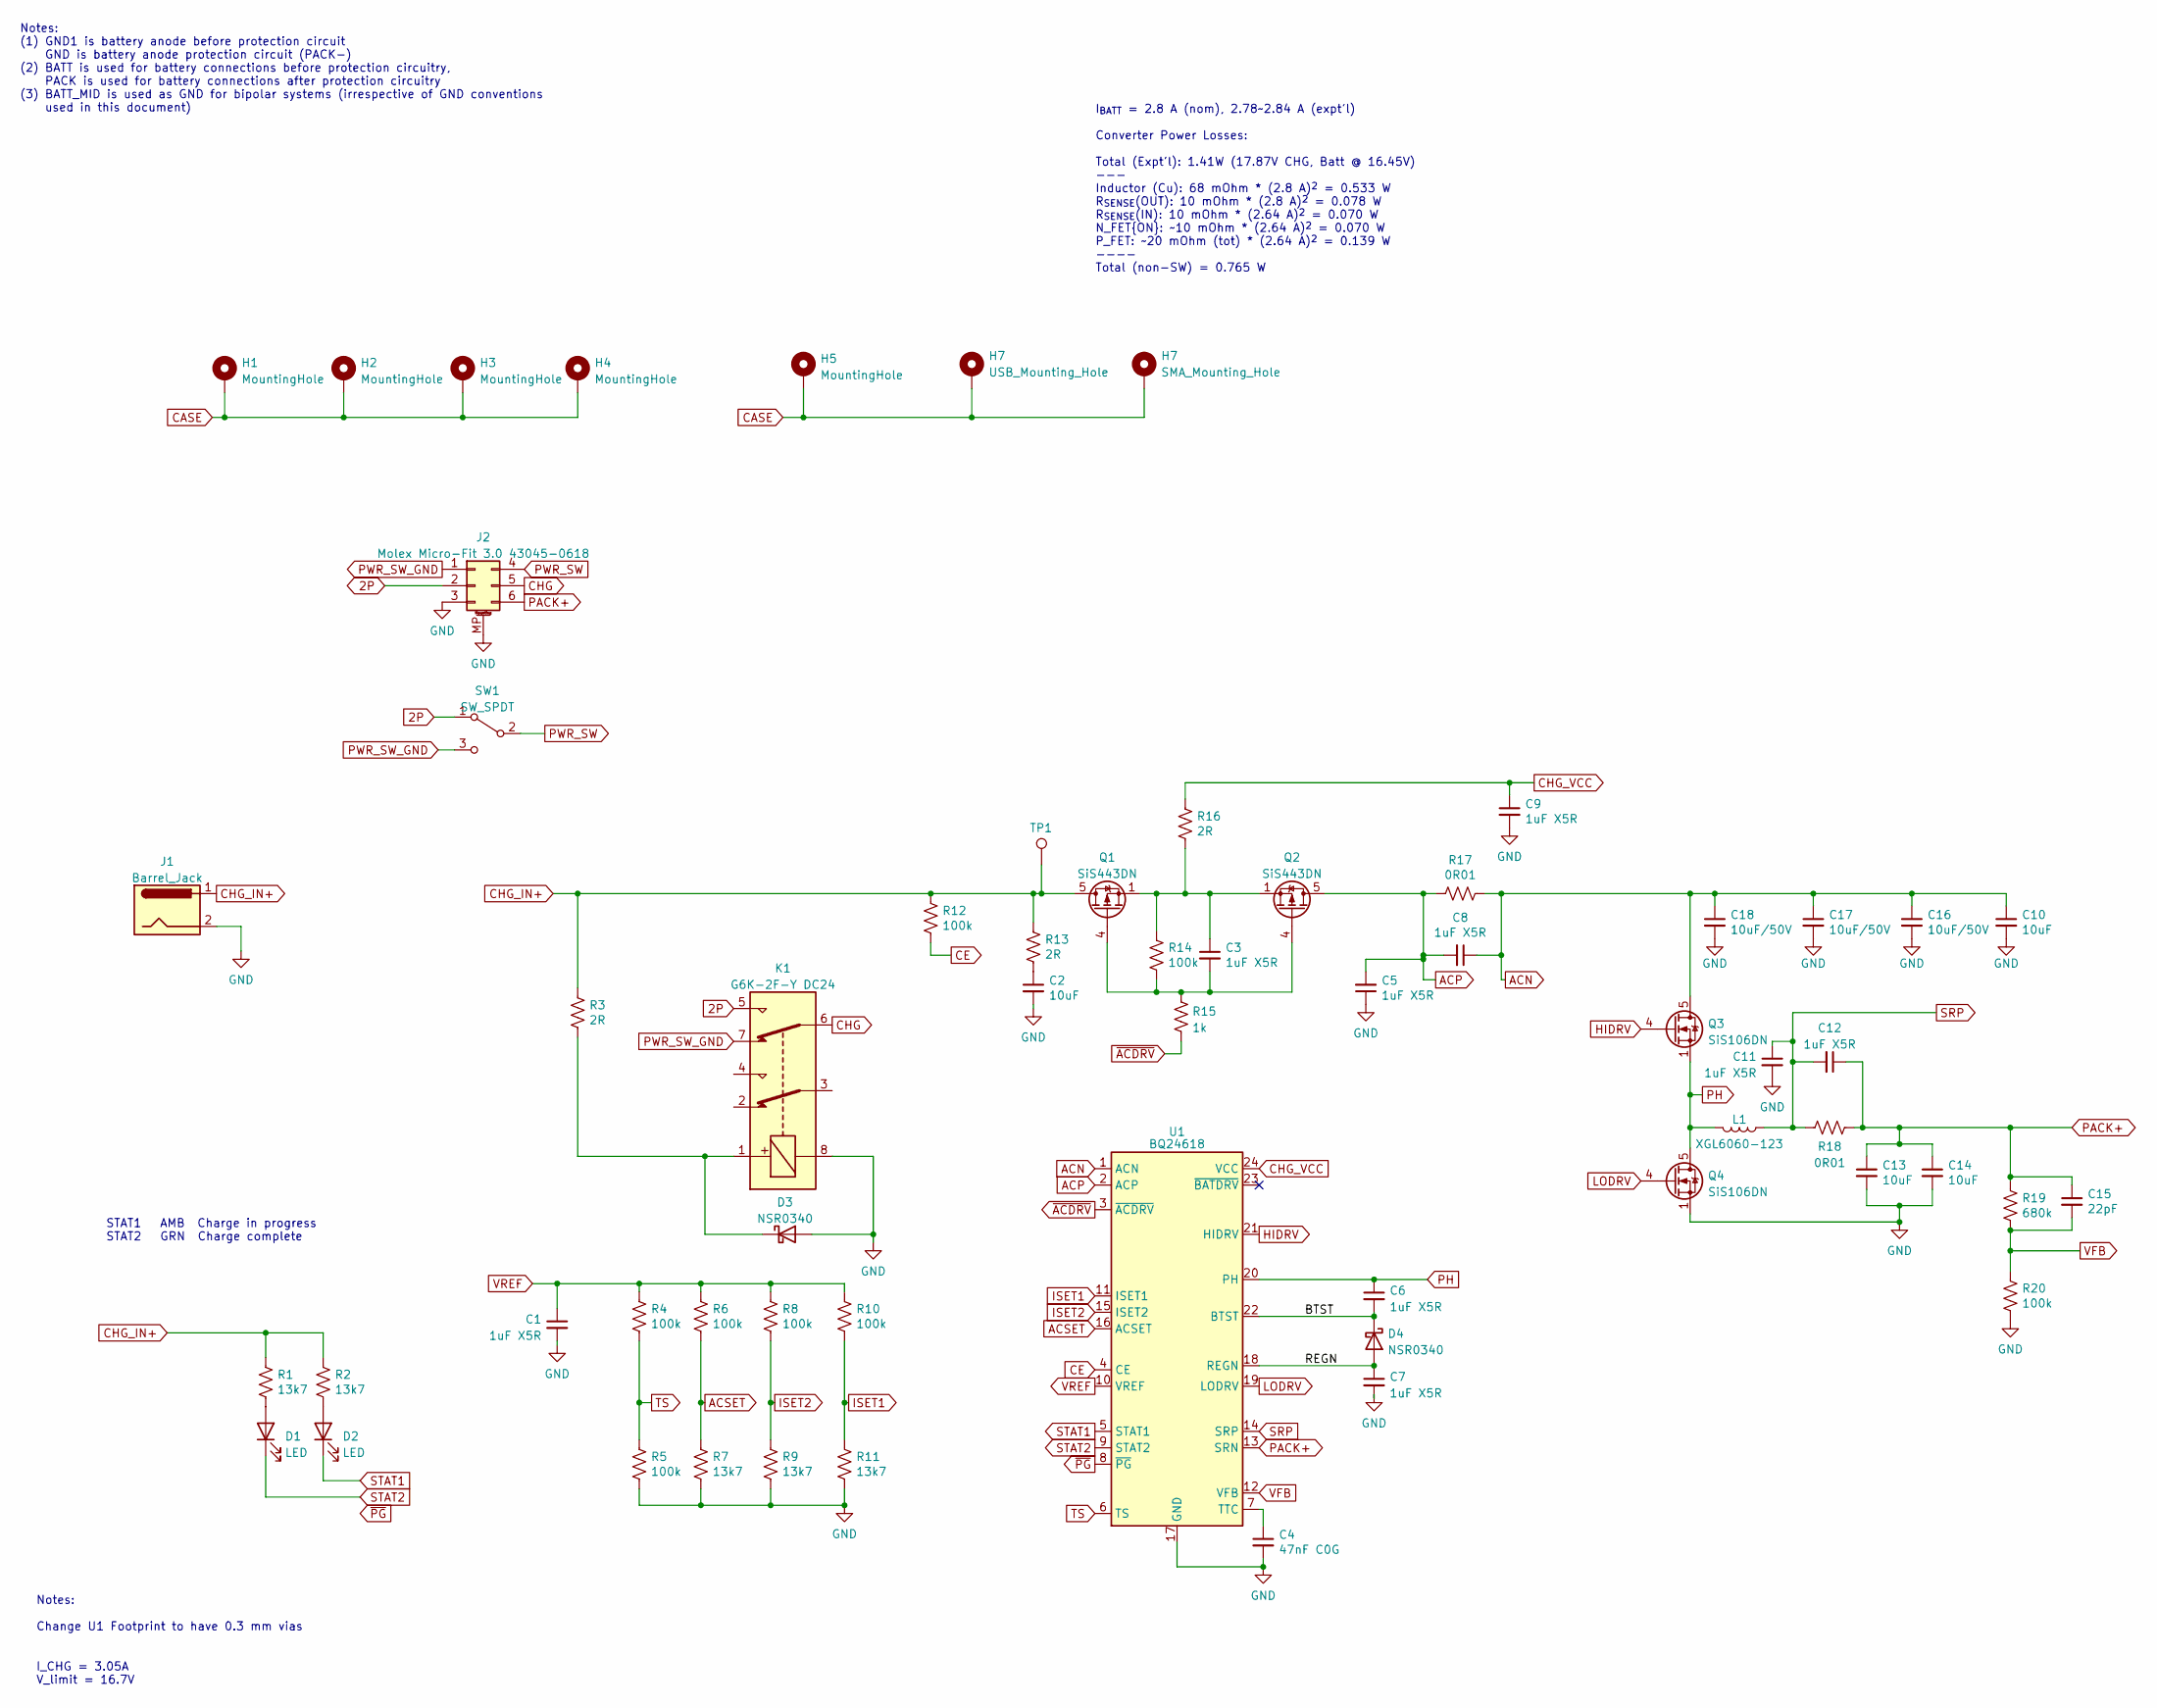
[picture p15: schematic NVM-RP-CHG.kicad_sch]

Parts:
C1, C3, C5, C6, C7, C8, C9, C11, C12: 1uF X5R; C_0402_1005Metric
C2, C10, C13, C14: 10uF; C_1206_3216Metric_Red
C4: 47nF C0G; C_0805_2012Metric_Red_outline
C15: 22pF; C_0402_1005Metric
C16, C17, C18: 10uF/50V; C_0805_2012Metric_Red_outline
D1, D2: LED; LED_Osram_Lx_P47F_D2mm_ReverseMount
D3, D4: NSR0340; D_SOD-523
H1, H2, H3, H4: MountingHole; MountingHole_4.3mm_M4_ISO14580_Pad
H5: MountingHole; PanelCutout_6.5mm_PTH
H7: USB_Mounting_Hole; PANEL_CUTOUT_MUSBK15230
J1: Barrel_Jack; BarrelJackDC_Switchcraft721_712
J2: Molex Micro-Fit 3.0 43045-0618; Molex_Micro-Fit_3.0_43045-0618_2x03-1MP_P3.00mm_Vertical
K1: G6K-2F-Y DC24; Relay_DPDT_Omron_G6K-2F-Y
L1: XGL6060-123; L_Coilcraft_XAL60xx_6.36x6.56mm
Q1, Q2: SiS443DN; Vishay_PowerPAK_1212-8_Single
Q3, Q4: SiS106DN; Vishay_PowerPAK_1212-8_Single
R1, R2, R7, R9, R11: 13k7; R_0402_1005Metric
R3, R13, R16: 2R; R_0603_1608Metric_red
R4, R5, R6, R8, R10, R12, R14, R20: 100k; R_0402_1005Metric
R15: 1k; R_0402_1005Metric
R17, R18: 0R01; R_1206_3216Metric
R19: 680k; R_0402_1005Metric
SW1: SW_SPDT; TestPoint_3Pads
TP1: TestPoint; TestPoint_Pad_D1.0mm
U1: BQ24618; HVQFN-24-1EP_4x4mm_P0.5mm_EP2.5x2.5mm

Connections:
2P: J2.2, K1.5, SW1.1 (A)
/BTST: C6.2, D4.1 (K), U1.22 (BTST)
/REGN: C7.1, D4.2 (A), U1.18 (REGN)
ACN: C8.1, C10.1, C16.1, C17.1, C18.1, Q3.5 (D), R17.1, U1.1 (ACN)
ACP: C5.2, C8.2, Q2.5 (D), R17.2, U1.2 (ACP)
ACSET: R6.2, R7.1, U1.16 (ACSET)
CASE: H1.1, H2.1, H3.1, H4.1, H5.1, H7.1; also elsewhere on the board
CE: R12.2, U1.4 (CE)
CHG: J2.5, K1.6
CHG_IN+: J1.1, Q1.5 (D), R1.1, R2.1, R3.2, R12.1, R13.1, TP1.1
CHG_VCC: C9.1, R16.2, U1.24 (VCC)
GND: C1.2, C2.2, C4.2, C5.1, C7.2, C9.2, C10.2, C11.2, C13.2, C14.2, C16.2, C17.2, C18.2, D3.2 (A), J1.2, J2.3, J2.MP (MountPin), K1.8, Q4.1 (S), Q4.2 (S), Q4.3 (S), R5.2, R7.2, R9.2, R11.2, R20.1, U1.17 (GND), U1.25 (EP)
HIDRV: Q3.4 (G), U1.21 (HIDRV)
ISET1: R10.2, R11.1, U1.11 (ISET1)
ISET2: R8.2, R9.1, U1.15 (ISET2)
LODRV: Q4.4 (G), U1.19 (LODRV)
unnamed: C2.1, R13.2
unnamed: C3.1, Q1.1 (S), Q1.2 (S), Q1.3 (S), Q2.1 (S), Q2.2 (S), Q2.3 (S), R14.1, R16.1
unnamed: D1.2 (A), R1.2
unnamed: D2.2 (A), R2.2
unnamed: D3.1 (K), K1.1, R3.1
unnamed: C3.2, Q1.4 (G), Q2.4 (G), R14.2, R15.1
unnamed: C4.1, U1.7 (TTC)
PACK+: C12.1, C13.1, C14.1, C15.1, J2.6, R18.1, R19.2, U1.13 (SRN)
PH: C6.1, L1.2, Q3.1 (S), Q3.2 (S), Q3.3 (S), Q4.5 (D), U1.20 (PH)
PWR_SW: J2.4, SW1.2 (B)
PWR_SW_GND: J2.1, K1.7, SW1.3 (C)
SRP: C11.1, C12.2, L1.1, R18.2, U1.14 (SRP)
STAT1: D2.1 (K), U1.5 (STAT1)
STAT2: D1.1 (K), U1.9 (STAT2)
TS: R4.2, R5.1, U1.6 (TS)
VFB: C15.2, R19.1, R20.2, U1.12 (VFB)
VREF: C1.1, R4.1, R6.1, R8.1, R10.1, U1.10 (VREF)
~ACDRV: R15.2, U1.3 (~ACDRV)
~PG: U1.8 (~PG)

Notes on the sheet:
I_{BATT} = 2.8 A (nom), 2.78~2.84 A (expt'l) Converter Power Losses: Total (Expt'l): 1.41W (17.87V CHG, Batt @ 16.45V) --- Inductor (Cu): 68 mOhm * (2.8 A)^{2} = 0.533 W R_{SENSE}(OUT): 10 mOhm * (2.8 A)^{2} = 0.078 W R_{SENSE}(IN): 10 mOhm * (2.64 A)^{2} = 0.070 W N_FET{ON}: ~10 mOhm * (2.64 A)^{2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
I_CHG = 3.05A V_limit = 16.7V
Notes: (1) GND1 is battery anode before protection circuit GND is battery anode protection circuit (PACK-) (2) BATT is used for battery connections before protection circuitry, PACK is used for battery connections after protection circuitry (3) BATT_MID is used as GND for bipolar systems (irrespect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
STAT1 AMB Charge in progress STAT2 GRN Charge complete
Notes: Change U1 Footprint to have 0.3 mm vias

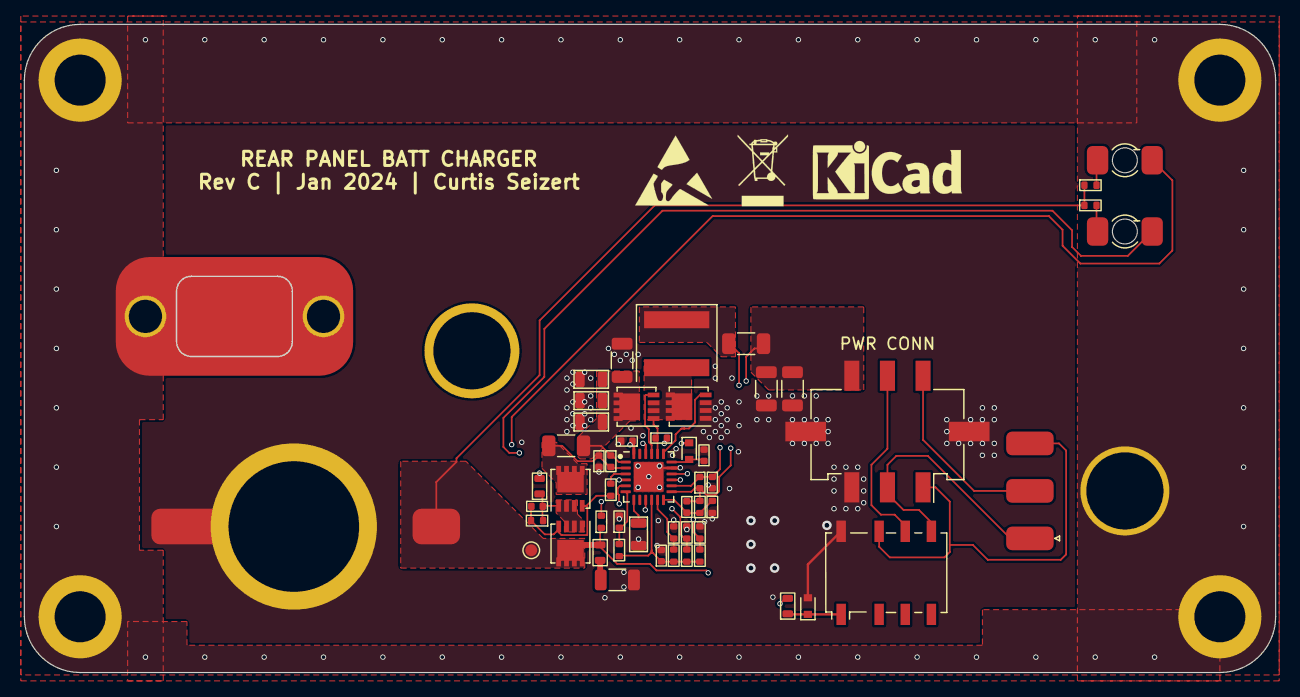
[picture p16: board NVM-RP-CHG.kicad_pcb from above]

Board: 4 copper layers, 105.4 x 54.6 mm, 60 parts (0 on the bottom side), 34 nets.

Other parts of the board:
H6: USB_Mounting_Hole; PANEL_CUTOUT_MUSBK15230

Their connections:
CASE: H6.1; also elsewhere on the board

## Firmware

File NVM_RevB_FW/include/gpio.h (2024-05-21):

#ifndef GPIO_H_
#define GPIO_H_

#include "stm32u5xx.h"
#include "stm32u575xx.h"

		

typedef enum{
	GPIO_PORT_A = 0U,
	GPIO_PORT_B = 1U,
	GPIO_PORT_C = 2U,
	GPIO_PORT_D = 3U,
	GPIO_PORT_E = 4U,
	GPIO_PORT_F = 5U,
	GPIO_PORT_G = 6U,
	GPIO_PORT_H = 7U,
} gpioPort_TypeDef;

typedef enum{
	GPIO_PIN_0	 = 0U,
	GPIO_PIN_1	 = 1U,
	GPIO_PIN_2	 = 2U,
	GPIO_PIN_3	 = 3U,
	GPIO_PIN_4	 = 4U,
	GPIO_PIN_5	 = 5U,
	GPIO_PIN_6	 = 6U,
	GPIO_PIN_7	 = 7U,
	GPIO_PIN_8	 = 8U,
	GPIO_PIN_9	 = 9U,
	GPIO_PIN_10	 = 10U,
	GPIO_PIN_11	 = 11U,
	GPIO_PIN_12	 = 12U,
	GPIO_PIN_13	 = 13U,
	GPIO_PIN_14	 = 14U,
	GPIO_PIN_15	 = 15U
} gpioPin_TypeDef;

typedef enum{
	GPIO_INPUT 	= 0U,
	GPIO_OUTPUT = 1U,
	GPIO_AF			=	2U,
	GPIO_ANALOG	=	3U
} gpioMode_TypeDef;

typedef enum{
	GPIO_PUSH_PULL	= 0U,
	GPIO_OPEN_DRAIN	=	1U
} gpioOtype_TypeDef;

typedef enum{
	GPIO_SPEED_LO	=			0U,
	GPIO_SPEED_MED	=			1U,
	GPIO_SPEED_FAST	=			2U,
	GPIO_SPEED_MAX	=			3U
} gpioSpeed_TypeDef;

typedef enum{
	GPIO_NO_PUPD		=			0U,
	GPIO_PULL_UP		=			1U,
	GPIO_PULL_DOWN		=			2U
} gpioPupd_TypeDef;

typedef enum{
	AF0 	= 0U,
	AF1 	= 1U,
	AF2 	= 2U,
	AF3 	= 3U,
	AF4 	= 4U,
	AF5 	= 5U,
	AF6 	= 6U,
	AF7 	= 7U,
	AF8 	= 8U,
	AF9 	= 9U,
	AF10 	= 10U,
	AF11 	= 11U,
	AF12 	= 12U,
	AF13 	= 13U,
	AF14 	= 14U,
	AF15 	= 15U,

} gpioAF_TypeDef;

typedef struct __GPIO_Init_TypeDef{
	gpioMode_TypeDef mode;
	gpioOtype_TypeDef otype;
	gpioSpeed_TypeDef ospeed;
	gpioPupd_TypeDef pupd;
} GPIO_Init_TypeDef;

typedef struct{
	GPIO_TypeDef * port;
	gpioPin_TypeDef pin;
} Pin_t;

typedef enum{
	GPIO_STATE_LO	=	0U,
	GPIO_STATE_HI	=	1U
} PinState_t;

Pin_t create_pin(GPIO_TypeDef * port, gpioPin_TypeDef pin);

void interrupt_config_rising(Pin_t gpio);
void interrupt_config_falling(Pin_t gpio);
void gpio_init_pin(Pin_t gpio, const GPIO_Init_TypeDef * init);
void gpio_config_af(Pin_t gpio, gpioAF_TypeDef AF);

void gpio_set_pin(Pin_t gpio);
void gpio_reset_pin(Pin_t gpio);
void gpio_set_state(const Pin_t gpio, PinState_t state);
PinState_t gpio_get_state(const Pin_t gpio);

#endif // GPIO_H_

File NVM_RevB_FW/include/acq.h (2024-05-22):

	/** acq.h
	 * 	Header file for high-level acquisition functions for NVM Rev B
	*/

#ifndef ACQ_H_
#define ACQ_H_

#include "stm32u5xx.h"
#include "stm32u575xx.h"
#include "sys_cfg.h"
#include "stdint.h"
#include "ad403x.h"
#include "ad5686.h"
#include "sinc.h"

#define ACQ_FLAG_GPIO_CDS				(1UL << 0)
#define ACQ_FLAG_GPIOCDS_SW1			(1UL << 1)
#define ACQ_FLAG_GPIOCDS_SW2			(1UL << 2)
#define ACQ_FLAG_GPIO_MOD				(1UL << 3)
#define ACQ_FLAG_GPIOMODPOL				(1UL << 4)
#define ACQ_FLAG_PARAM_SETUP			(1UL << 5)
#define ACQ_FLAG_MODTIMRDY				(1UL << 6)
#define ACQ_FLAG_MOD_ON					(1UL << 7)
#define ACQ_FLAG_GPIOMOD_SET			(1UL << 8)
#define ACQ_FLAG_GPIOCDS_SET			(1UL << 9)

#define RELAY_K1_SET					(1UL << 1)
#define RELAY_K2_SET					(1UL << 2)
#define RELAY_K3_SET					(1UL << 3)

#define OVERRANGE_FLAG					1UL << 10
#define ADC_OVERRANGE_FLAG				1UL << 11
#define HI_GAIN_FLAG					1UL << 12
#define SEND_UART_FLAG					1UL << 13
#define SKIP_VOS_DAC_UPDATE_FLAG		1UL << 14
#define BLOCK_SYNC_ERROR_FLAG			1UL << 15 // If ADC blocks are not aligned with mod cycles
#define NULL_ENABLE						1UL << 16
#define ACQ_FLAG_SET_NULL				1UL << 17

#define AD403X_MAX_ARRAY_LEN			256

#define DATA_FLAG_DATA_INVALID			(1U << 0)
#define DATA_FLAG_WAIT_FOR_CYCLE		(1U << 1)

#define AD403X_CODE_SPAN				(1UL << 30)

typedef struct{
	int32_t buf[AD403X_MAX_ARRAY_LEN];
	uint16_t index;
	uint16_t bufsize;
	int16_t phase[2];		// phase[1] gets copied to phase[0] when block
							// is processed
}AD403XData_t;

typedef struct{
	double v_null_lo;
	double v_null_hi;
	double v_ref;
	double gain_lo;
	double gain_hi;
}AcqConst_t;

typedef enum{
	GAIN_STATE_LO,
	GAIN_STATE_HI
}GainState_t;

/// @brief Struct containing the parameters for an acquisition
typedef struct{
	AcqConst_t * acq_const;
	SincFilter_t * sinc;
	AD403XData_t * adc_data;
	const AD403X_t * adc;
	
	int64_t accum;

	int32_t mod_deadtime_cyc;
	int32_t demod_deadtime_cyc;
	uint32_t adc_samp_freq;
	int32_t offset_accum;
	uint32_t flags;
	
	float mod_freq; 
	float mod_deadtime_us;
	float demod_deadtime_us;
	float settle_time_us;
	float Vos_dac_deadband_nV;
	float v_os;

	uint16_t offset_counter;
	uint16_t code_deadband;			// 
	uint16_t mod_cycles_per_avg;	// number of modulator cycles per average value
	uint16_t mod_cycles_per_update; // number of modulator cycles per Vos DAC update
	uint16_t mod_cycles_per_cds;	// number of modulator cycles per ADC input reversal
	uint16_t log2SampAvg;
	uint16_t cnv_cycles;
	uint16_t blocks_per_cycle;
	
	uint16_t relay_states;
	uint16_t array_size;

	uint16_t sinc_order;

	GainState_t gain_state;
	
}AcqParam_t;

typedef enum{
	MOD_PHASE_0		= 0,
	MOD_PHASE_1		= 1
} ModPhase_t;

#define SW1_Pos 	0
#define SW2_Pos		1

typedef enum{
	SW1_CM_SW2_CM	= 0,
	SW1_IN_SW2_CM	= (1U << SW1_Pos),
	SW1_CM_SW2_IN	= (1U << SW2_Pos),
	SW1_IN_SW2_IN	= (1U << SW1_Pos) | (1U << SW2_Pos)
} CDSPhase_t;

typedef enum{
	BLOCK_NO_ERROR			= 0,
	BLOCK_SYNC_ERROR		= 1,
	BLOCK_OVERRANGE_ERROR	= 2,
	BLOCK_SYNC_OVR_ERROR	= 3
} BlockErr_t;

	// HIGH LEVEL FUNCTIONS
void setup_acquisition(AcqParam_t * acq);
void start_acquisition(AcqParam_t * acq);
void pause_acquisition(AcqParam_t * acq);
void pause_acquisition_diagnostic(AcqParam_t * acq);

	// SWITCH STATE-RELATED FUNCTIONS
void gpio_mod_clocks(AcqParam_t * acq);
void gpio_cds_clocks(AcqParam_t * acq);
void set_mod_phase(AcqParam_t * acq, ModPhase_t phase);
void set_cds_phase(AcqParam_t * acq, CDSPhase_t phase);
void tim_mod_clocks(AcqParam_t * acq);
void tim_cds_clocks(AcqParam_t * acq);
ModPhase_t get_mod_phase(void);
CDSPhase_t get_cds_phase(void);
CDSPhase_t gen_cds_phase(uint16_t p1, uint16_t p2);

	// GAIN-RELATED FUNCTIONS
void set_gain(AcqParam_t * acq, GainState_t gain);
double get_analog_gain(AcqParam_t * acq);
float getLSBSize_nV(double gain);

	// NULL COMPENSATION FUNCTIONS
void set_null(AcqParam_t * acq, double v_avg);
double subtract_null(AcqParam_t * acq, double v_avg);

	// DATA PROCESSING FUNCTIONS
double get_block_v_avg(AcqParam_t * acq);
double adc_code_to_volts(AcqParam_t * acq, int64_t code);
void process_data_cycle(AcqParam_t * acq);
int16_t calculate_vos_dac_increment(AcqParam_t * acq);
double get_block_v_avg(AcqParam_t * acq);
inline BlockErr_t check_block_sync(void);
int64_t get_code_average(const AD403XData_t * data);
int32_t get_code_offset(const AD403XData_t * data);
void ad403x_data_update_phase(AD403XData_t * data);

	// MISCELLANEOUS FUNCTIONS
void queue_dac_write(AD5686Channel_t ch, uint16_t code);
void set_relay_defaults(void);

#endif // ACQ_H_

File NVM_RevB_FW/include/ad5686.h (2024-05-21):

	
	/*	Basic driver for AD5686 in NVM Rev B
	*
	*
	*/

#ifndef AD5686_H_
#define AD5686_H_

#include "stdint.h"
#include "stm32u575xx.h"
#include "stm32u5xx.h"

/* Note: Command defines are aligned with the first byte of the transfer */

	/* COMMAND DEFINES */
#define AD5686_WRITE_DAC			0x01 << 4
#define AD5686_UPDATE_DAC			0x02 << 4
#define AD5686_WRITE_UPDATE		0x03 << 4
#define AD5686_TOGGLE_POWER		0x04 << 4
#define AD5686_NLDAC_MASK_REG	0x05 << 4
#define AD5686_SW_RESET				0x06 << 4
#define AD5686_DCEN						0x08 << 4		// Daisy chain enable
#define AD5686_READBACK				0x09 << 4
#define AD5686_NO_OP					0x0F << 4

	/* ADDRESS DEFINES */
typedef enum{
	AD5686_DAC_A					= (1U << 0),
	AD5686_DAC_B					= (1U << 1),
	AD5686_DAC_C					= (1U << 2),
	AD5686_DAC_D					= (1U << 3)
}AD5686Channel_t;

	/* OUTPUT DEFINES */
#define MOD1_HI_DAC					AD5686_DAC_A	// Output A
#define V_OS_DAC					AD5686_DAC_B	// Output B
#define MOD2_HI_DAC					AD5686_DAC_C	// Output C
#define MOD_LO_DAC					AD5686_DAC_D	// Output D

	/* REPEAT USE DEFINES */
#define AD5686_WRT_UP_DAC_A		(AD5686_WRITE_UPDATE | AD5686_DAC_A)
#define AD5686_WRT_UP_DAC_B		(AD5686_WRITE_UPDATE | AD5686_DAC_B)
#define AD5686_WRT_UP_DAC_C		(AD5686_WRITE_UPDATE | AD5686_DAC_C)
#define AD5686_WRT_UP_DAC_D		(AD5686_WRITE_UPDATE | AD5686_DAC_D)

	/* DEFAULT DAC OUTPUTS */
#define MOD1_HI_DEFAULT				65535U	// 2.50V
#define MOD2_HI_DEFAULT				65535U	// 2.50V
#define V_OS_DEFAULT					0x4B80
#define MOD_LO_DEFAULT				20000U

#define AD5686_NUM_CHANNELS			4U

typedef struct{
	SPI_TypeDef * spi;
	DMA_Channel_TypeDef * dma;
	uint32_t channel_codes[AD5686_NUM_CHANNELS];
}AD5686_t;


void ad5686_set_spi_bus(AD5686_t * dac, SPI_TypeDef * spi);
void ad5686_write_dac(AD5686_t * dac, AD5686Channel_t ch, uint16_t code);
uint32_t ad5686_format_data_write(AD5686Channel_t ch, uint16_t code);

void ad5686_write_all(AD5686_t * dac);

#endif //AD5686_H_

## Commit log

2024-01-30 Initial commit of kicad design files
    [ADC.kicad_sch, ADR1399ref.kicad_sch, GateDrives.kicad_sch, Inputsentry.kicad_sch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]
2024-01-30 Added battery design files
    [Batt_Rev21.kicad_pcb, Batt_Rev21.kicad_sch, Batt_Rev21.sch]
2024-02-19 Update README.md
    Added current status section
2024-04-03 Update README.md
    Added principle of operation and some results from testing the board.
2024-05-21 Update README.md
    Updated current status
